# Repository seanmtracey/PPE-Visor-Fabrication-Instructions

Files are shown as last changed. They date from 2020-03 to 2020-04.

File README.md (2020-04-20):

# Visors

This document provides a list of materials and instructions for constructing a face visor to help prevent contraction of infectious diseases. At the end of the document are contact details for coordinating the distribution of the visors.

This is the printed visor when assembled with acetate and elastic:

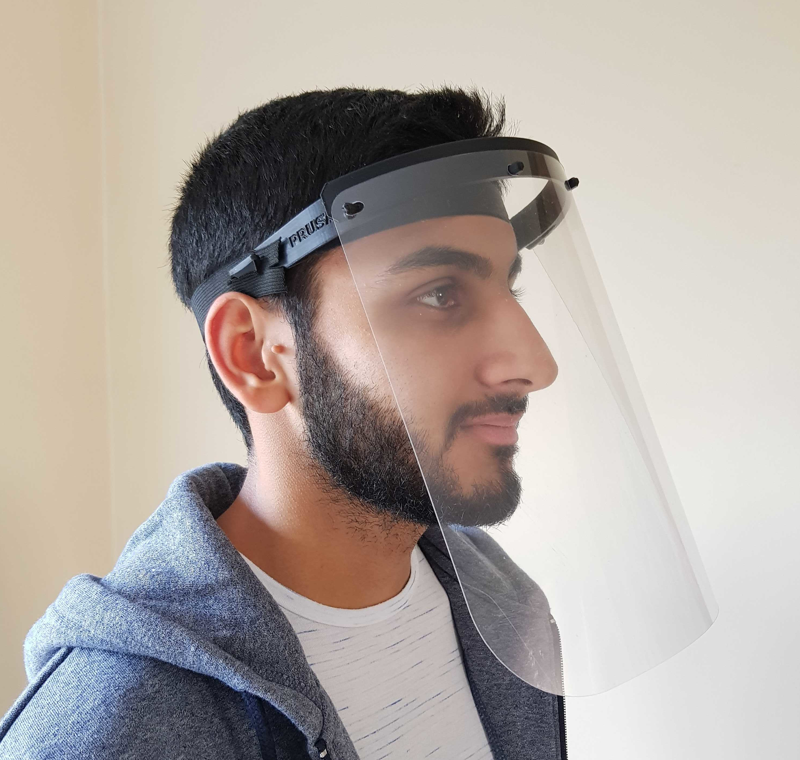
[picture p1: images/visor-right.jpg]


## Note for medical professionals

If you are an NHS worker, and you would like to add your details as a point of contact to receive these visors, please see the contact section at the end of this document.

## Required tools and materials for constructing the visor

- A 3D printer with a print space of at least 187mm by 147mm by 21.5mm

- At least 10 metres of either PETG, PLA, or ABS print filament. PETG is our preferred filament type, but both PLA and ABS are fine.

## Specifications

To standardise our printing and assembly processes, we need to ensure we’re all printing the same version of the same file and using the right acetate etc.

### Visor 3D printing files

Print the Prusa rc3 which you can find in `covid19_headband_rc3.stl` at https://www.prusaprinters.org/prints/25857/files To save filament, you can instead print this modified version of the Prusa rc3 from https://www.prusaprinters.org/prints/29080-prusa-rc3-m2/files

If you would like to stack the standard Prusa rc3 prints, try one of the files at https://www.prusaprinters.org/prints/27975-prusa-rc3-faceshield-remix-stacked 

Other files from the Prusa website may be used but please run it by Dhiresh before printing.

We aren't printing the bottom part of the Prusa RC3 model because it doesn't appear to provide much benefit and is tricky to print and assemble accurately.

### Acetate sheets

If you don’t have any acetate please leave this to Anup, Abhi, and Gwilym, who have rotary machines cutting all the sheets for us. All parts should be sent to Dhiresh (London Hub) or Gwilym and Ellie (Hampshire Hub) for assembly.

If you do have acetate, the acetate should be 400 microns thick, and the dimensions for the sheet should be 290mm x 240mm. The longer side going across the headband.

To prepare the acetate:
1. Cut acetate 290mm across by 240mm vertical.
2. Find the mid-point (145mm), mark with sharpie.
3. Measure 70mm out each side of mid-point, mark dots with sharpie.
4. Use a normal double-hole punch, centred on each of those dots, to make 2 pairs of holes.
5. Start at one end and clip the 4 perfectly aligned holes onto the pins.

### Elastic

The elastic should be 340mm long. Cut a slit near each end of the elastic about 1cm long (fold it and cut a 5mm slit into the fold). Push the large peg on the side of the headband through a slit to attach the elastic; repeat for the other side with the other end of the elastic.

## How to print

The following instructions describe how to print using Automaker software with the CEL Robox printer, which some of our group use.

For other makes of printer:

- [Cura software instructions](cura.md)
- Neil Sewell of Solid Print3D has written instructions for printing the visor with the popular [Ultimaker](https://www.solidprint3d.co.uk/a-guide-to-printing-face-shields-battling-covid19-one-3d-print-at-a-time/)  range of 3D printers.

### Step 1. Loading the STL

First download the STL file listed above to your computer, then open up the AutoMaker software:

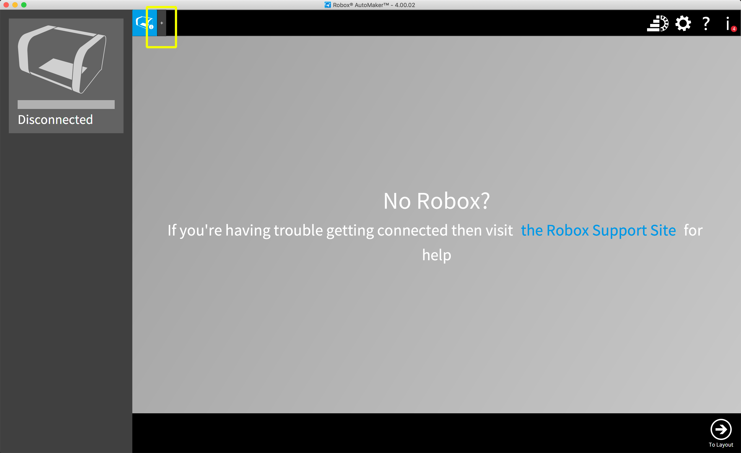
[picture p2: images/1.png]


Along the top of the application, there is a toolbar of tabs, to the right of any open tabs, click the **+** icon (highlighted in yellow) to begin the process of loading your STL file. This opens a new tab with that says "Load a model" in the center of the view:

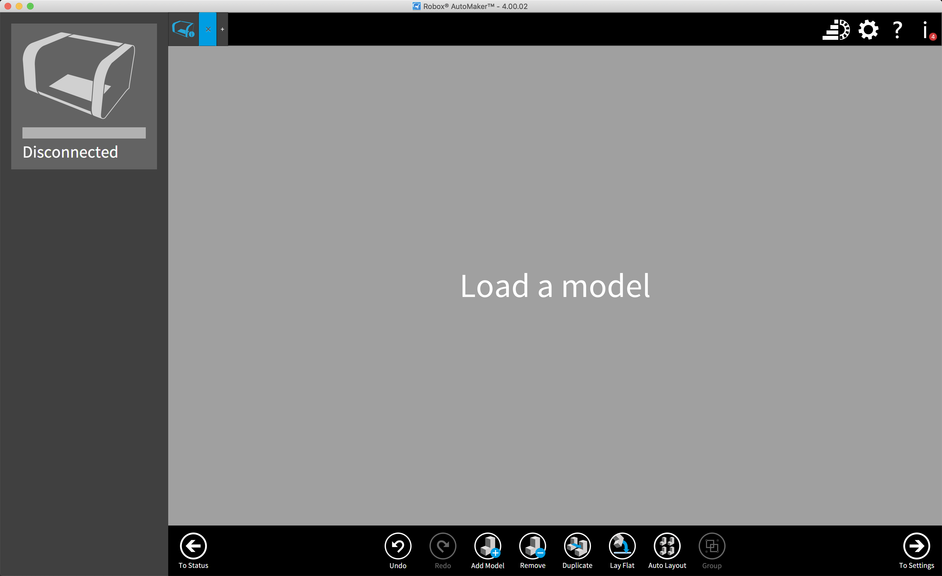
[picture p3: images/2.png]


Click the **Add Model** button in the bottom-middle of the view and browse for the STL file that you downloaded (or just drag-and-drop the STL file into the window):

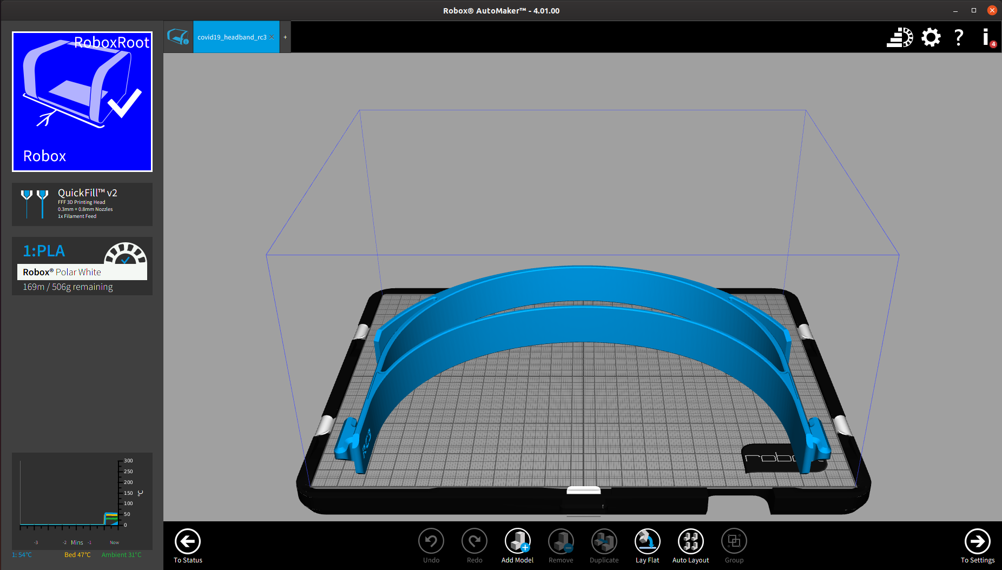
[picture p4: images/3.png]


### Step 2. Configuring the print

Once your model has been loaded and positioned by the AutoMaker software, you can configure the density of your print. We don't need a fine resolution print for the visor, so we use the preset options for the coarsest print. It takes about 2 hours to print one visor.

Click the **To Settings** button at the bottom-right corner of the AutoMaker software to go through to the final configuration steps of the print.

Select the first radio button (highlighted in green) to select the coarsest print. Do not enable any other options:

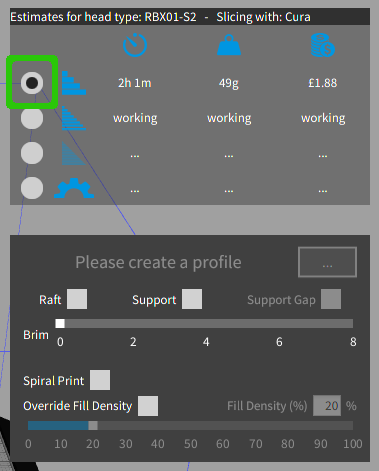
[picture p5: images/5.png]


### Step 3. The print

We're now ready to start printing the visor. If you have spray adhesive, apply it to the print bed now, this helps prevent warping as the visors are printed. If you don't have the adhesive, keep an eye on the print to make sure that nothing goes awry during the printing process.

Click the **Make** button in the bottom-right corner to start the print. The model is transferred to your printer and the print begins.

### Step 4. Removing the printed visor

When the print has completed, wash your hands with soap and wear gloves, if possible, to you handle the print. Also wash any tools you use to remove the print from the printer and tidy it up.

Check there are no sharp bits on the headband where they will be uncomfortable, or strings hanging off. Trim with a sharp knife as necessary.

## How to package

Wash your hands. Package the print in clean bags. You can put multiple visors in the same bag but package different materials separately (eg put PETG prints in a separate bag from PLA prints). Ideally put the bag in another bag or box as well as this will help prevent contamination during transport.

On the bags write:

- The material used in the print (PETG, PLA, or ABS)
- Your email address or name so you can be contacted if necessary
- The date that the print was packaged. The date is important because it is known that COVID-19 can live for up to three days on surfaces. Dhiresh will not open your visors for three days after you packaged them, and then will not deliver the finished visors for three days after he last touched them.

If you are providing the acetate part as well, do not send the visor assembled (to avoid damage). Instead, package the prepare acetate along with the 3d printed visor.

## Where to send

Send your printed visors to Dhiresh for assembly. He will then send them on to the people who requested them. Contact Dhiresh for his postal address.

## Contact Details

Makers for the NHS
 - Email: makers4thenhs@gmail.com
 - Twitter: https://twitter.com/makers4thenhs

## List of Contributors + Roles

### Volunteer Makers

- Sean M. Tracey: Team Co-ordinator / Backup Logistics
    - Twitter: https://twitter.com/seanmtracey

- Dhiresh Nathwani: Chief Designer and Founder
    - Twitter: https://twitter.com/dhireshnathwani

- Ellie Paine: Head of Communications
    - LinkedIn: https://www.linkedin.com/in/ellie-paine-6186a889

- Gwilym Newton: Head of Logistics
    - Twitter: https://twitter.com/trevelyan_panda
    - Site: https://researcher.watson.ibm.com/researcher/view.php?person=uk-GWILNEW

- Laura Cowen: Head of Documentation / Backup Communications

- James Sutton: Chief Liaison Officer

- Abhi Patel: Chief Financial Officer / GoFundMe Co-ordinator
    Twitter: https://twitter.com/technoidabhi
    LinkedIn: www.linkedin.com/in/technoidabhi

- Anup Chavda - Chief Blade Person: 
    - Twitter: https://twitter.com/anupchavda
    - LinkedIn: https://www.linkedin.com/in/anupchavda/

- Andy Stanford-Clark (IBM UK)
    Twitter: https://twitter.com/andysc

- Andreas Haimboeck-Tichy

- Arturs Grigals

- Benjamin Dyer

- Chris Dudley

- Chris Polin

- Christopher Grilli

- Dan Robinson

- Eoin Devane
    - LinkedIn: https://uk.linkedin.com/in/eoindevane

- Gabriel Orghidan

- Gary Barnett

- Jane Stockdill-Mander

- John Galvez

- John H Simpson

- Lucas Ferreira-Correia

- Luke Eustace

- Mark Lawson

- Michael Glass

- Mike Feingold

- Niall Beard

- Paul Crouch

- Pete M

- Ralph Bolton

- Richard Snell

- Romy Greenfield
    - LinkedIn: https://www.linkedin.com/in/romy-greenfield/
    - GitHub: https://github.com/anywhereiromy

- seanmtracey

- Selina Lee

- Stephen Porton

- Stuart Bayliss

- Sumit Maitra

- Simon Kapadia
    - Website: http://kapadia.pl

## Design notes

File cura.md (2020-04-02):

# Instructions for Printing with Cura

If you're using the (very excellent) [Cura](https://ultimaker.com/software/ultimaker-cura)
software to slice and print, then these instructions should help you print the PPE Visor.
Please also read the other instructions about printing too though - there's lots of
information in there about safe handling (and safe printing environments), packaging etc.
Since we're trying to prevent the spread of Coronavirus, please make sure you take appropriate
precautions to avoid spreading it on the visor!

## Prepare for Printing

When you open Cura, it should look something like this:

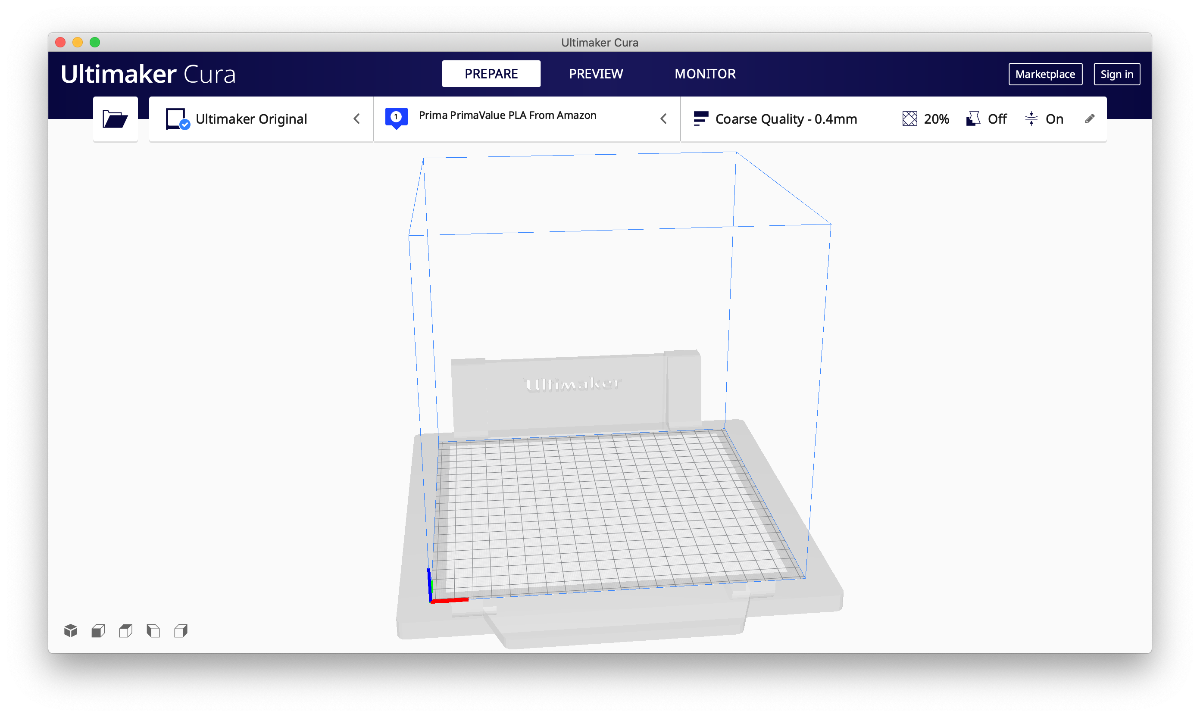
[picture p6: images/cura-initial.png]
Cura opening screen


I'm assuming you've used Cura before and it's set up for your printer. Next, load the visor
model (File -> Open File -> VISOR.STL). It should look like this:

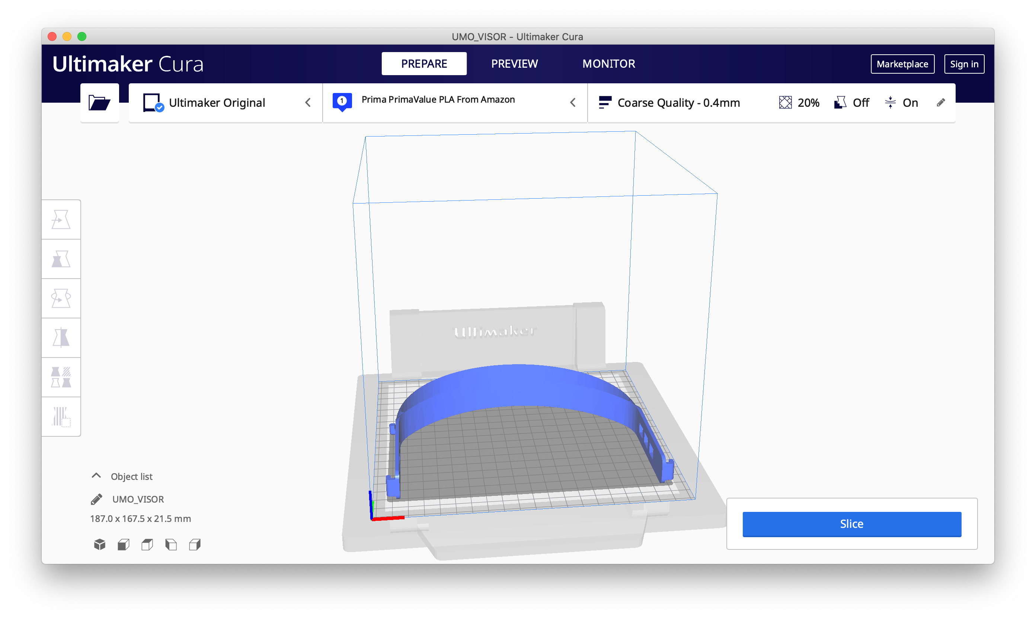
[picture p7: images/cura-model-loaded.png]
Cura model loaded


Next, select the printing profile (top right). The default settings for "draft quality" are
ideal for printing the visor (quality isn't that important):

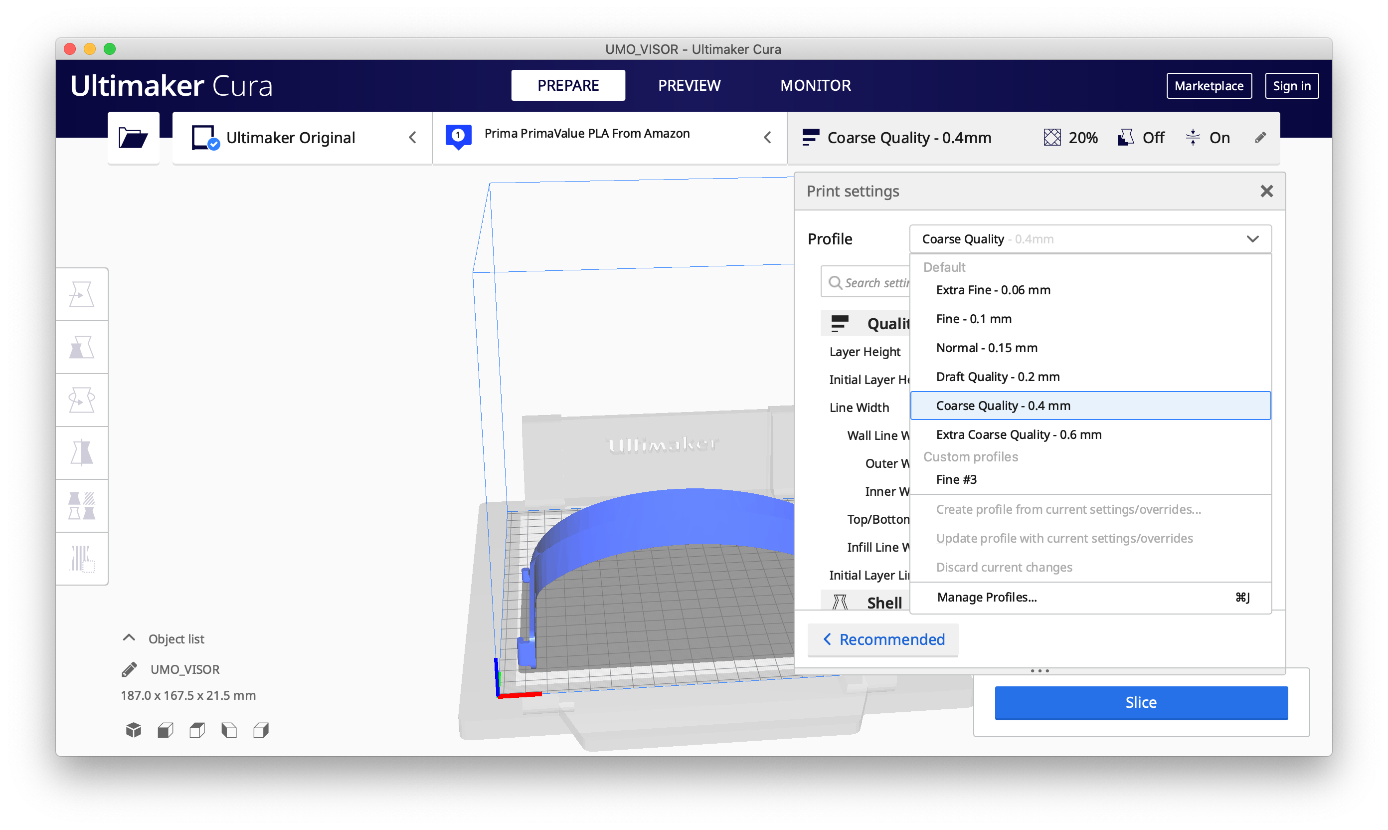
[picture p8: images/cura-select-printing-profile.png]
Select Cura printing profile


Some changes to the defaults are required:
 * 0.4mm layers
 * 20% infill is the default, but 30% is preferred
 * 60mm/s print speed
 * "skirt" bed adhesion, or no adhesion

Additionally ensure you've selected the correct material to print with (PETG is preferred but
not all printers can print with it, PLA is fine and ABS is also okay). If there are any other
settings you need to use that are specific to your printer then set them now.

The print is big and wide and quite thin - and so very prone to warping. If you have a
heated bed you'll need to use it, otherwise you may need adhesive on the blue painters tape.
Printing with a brim will also avoid warping, but you'll need to remove the brim after
printing (please observe handling precautions!). Ideally print with a skirt or no adhesion
as it means less work after the print is complete, but a warped print is less use than one
that you've had to trim.

Lastly, prepare for printing - press "Slice" (bottom right). You should see something
like this:

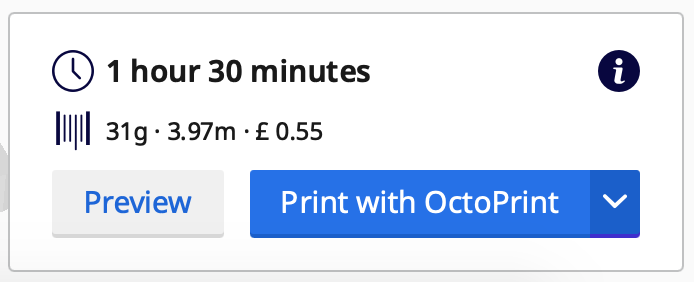
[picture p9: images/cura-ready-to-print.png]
Ready to print


## Printing

In my case I print with Octoprint, but you should use whatever method to print you
normally use.

Each print should take approximately 1 hour 30 minutes, and uses about 4 metres of
3mm filament.

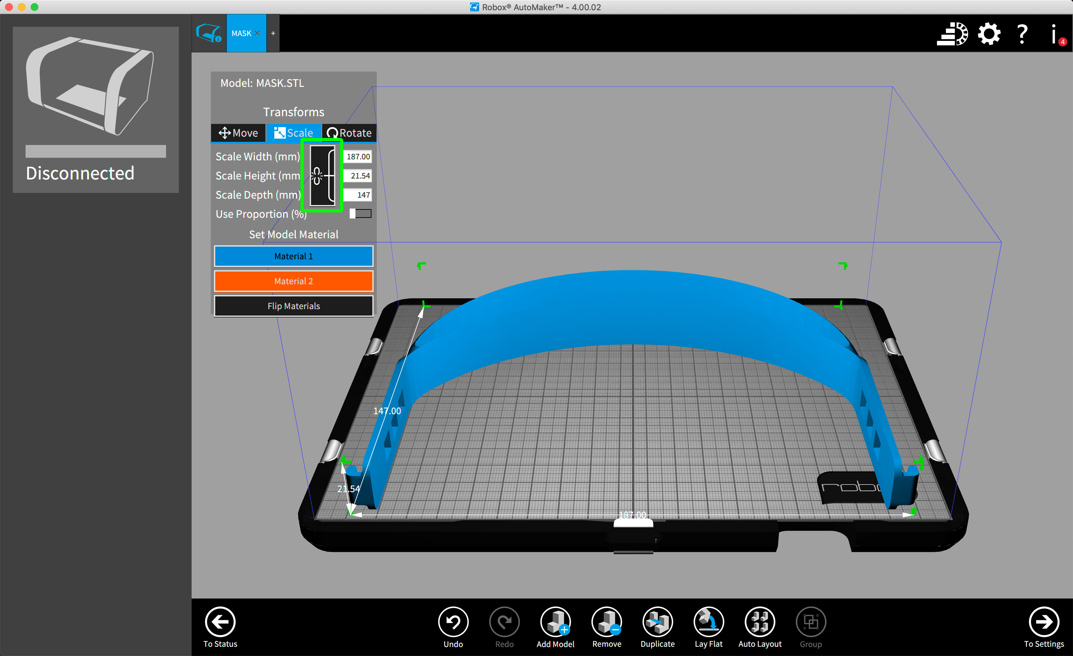
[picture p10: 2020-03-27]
images/4a.png

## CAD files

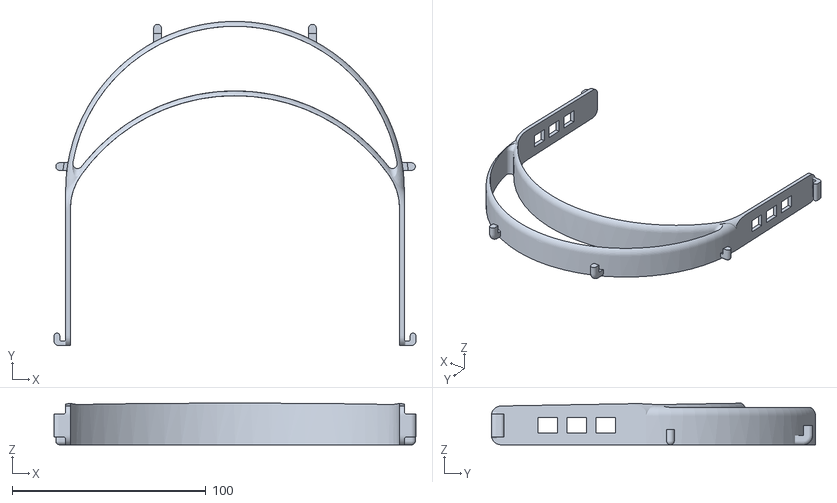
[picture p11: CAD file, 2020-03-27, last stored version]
VISOR.STL
187.0 x 167.5 x 21.5

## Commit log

2020-03-27 Add MASK.stl
    [MASK.STL]
2020-03-31 They're visors, not masks.
    [VISOR.STL]
2020-04-02 Added notes about standardised prints
2020-04-03 To avoid confusion just delete this?
    [VISOR.STL]
2020-04-03 Add PETG
    And a pecking order for print filaments
2020-04-09 Reduce elastic length
    Feedback from nurses is that 370mm is too long and the visor can slip. 340mm should address this.
2020-04-14 Updates to spec
    - Link to different stack design.
    - Add link to lighter/smaller version of the RC3 design.
    - Added mention of Hampshire Hub.
    - Add thickness of acetate
    - Add new dimensions of acetate (to wrap further round the head)
    - Add AndySC's instructions for preparing the acetate.
    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
